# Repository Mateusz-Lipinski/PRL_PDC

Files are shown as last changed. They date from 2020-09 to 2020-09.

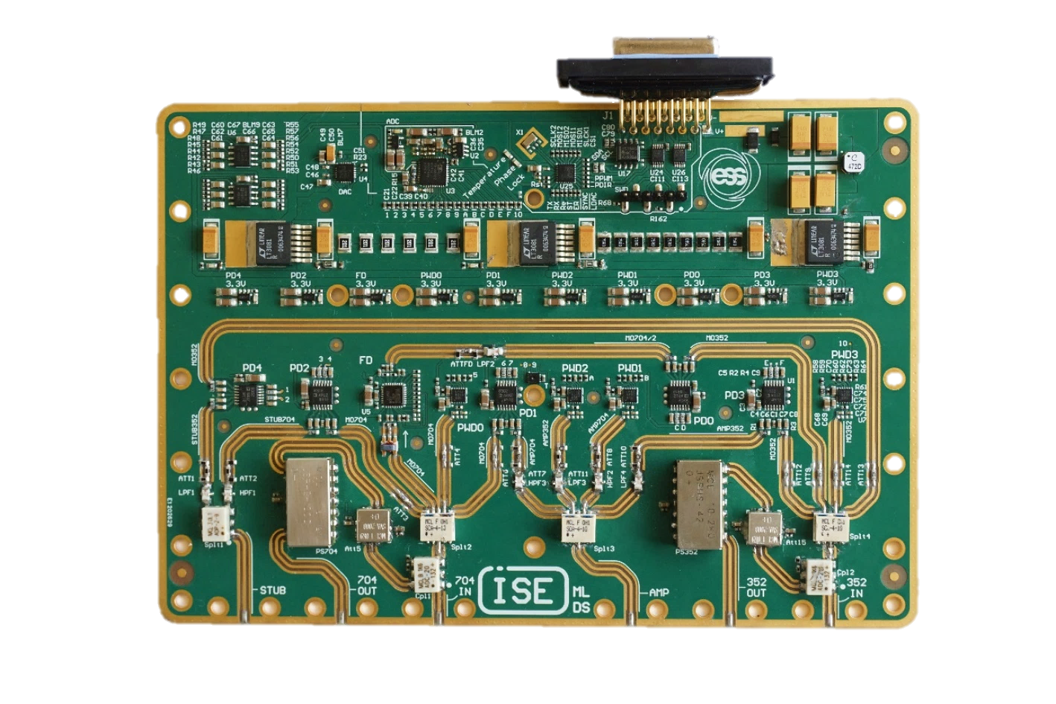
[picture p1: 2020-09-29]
płytka.png

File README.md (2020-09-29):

# PRL_PDC

Działanie układu aktywnej kompensacji dryftów opisałem w swojej pracy magisterskiej. Na płytce dodane są jeszcze regulowane tłumiki przed przesuwnikami fazy, do stabiizacji mocy.

Przesuwniki fazy i tłumiki są sterowane ze wzmacniaczy sumujących 2 sygnały z DAC z różnymi wzmocnieniami, co pozwala na sterowanie zgrubne i precyzyjne, w zakresie 0 - 12V. Wzmacniacze zostały wymienione na wszystkich płytkach i w projekcie, bo poprzednie wymagały symetrycznego zasilania. Innych błędów w projekcie nie znalazłem.
Z tego co wiem to rozwiązanie działa całkiem dobrze. Jak to działa można zobaczyć w symulacji w ./symulations.

Przestrajanie w tak szerokim zakresie jest potrzebne, żeby ustawić punkt stabilizacji w odpowiednim miejscu na charakterystyce detektorów (chyba najlepiej w połowieu)
Wskazania detektorów PD1 i PD2, oraz PD3 i PD4 są ze sobą powiązane, więc napisałem algorytm który przeszukuje charakterystykę i minimalizuje błąd średniokwadratowy, tak żeby oba detektory pracowały jak najbliżej środka charakterystyki. Działa to chyba w miarę ok, ale zdażyło się raz czy dwa że ustawił się taki punkt pracy że sterowanie się nasyciło - zależy od rzeczy podłączonych do układu.

Zauważyłem problem, polegający na tym, że przy przestrajaniu przesuwnika od jednego kanału (na jednej częstotliwości), zmieniaja się również wskazania detektorów na drugiej częstotliwości. Problem występował w prototypie, ale zwarcie wejść sterujących przesuwnikow (mają po 2 wejścia BIAS) wydawało się rozwiązać problem (nie wiem z czego to wynika, tymbardziej że piny wydają się byc zwarte w środku scalaka.
Ja podejrzewam że filtry są za słabe i detektory zbierają też drugą częstotliwość, co wpływa na pomiar fazy. Żeby to potwierdzić trzeba by niestety ciąć ścieżki i dołożyć dodatkowe filtry przed detektorami fazy. Można było zrobić miejsce na to na etapie projektu, ale z jakiegoś powodu podjęliśmy decyzję żeby tego nie robić.
(Minimializacja strat?)

W związku z powyższym, pętle stabilizacji fazy włączane pojedynczo wydają się działać, ale razem - zakłócają się nawzajem. W prototypie powodowało to że dryf fazy nie był kompensowany i wręcz ulegał wzmocnieniu.

Gdy próbowałem uruchomić stabilzację mocy, również występował problem zakłócania się pętli. Zmiana tłumienia powoduje zmianę fazy, a fazy zmianę tłumienia. Przez to obie pętle wariowały. W tym wypadku to jest raczej kwestia nastaw PID.

Stabilizacja temperatury działa, ale nie bardzo daje się schłodzić ten układ, nawet z radiatorem. Stabilizowałem na 35\*C - to trochę dużo. Nie wiem jakie warunki będą w docelowym racku. Precyzja stabilizacji jest bardzo dobra moim zdaniem.

Przy odkręcaniu kabli urywają się złącza SMA - lutowanie chyba pomaga.

Mikrokontroler programuje się przez wewnętrzne złącza SWD za pomocą ST-Link, albo przez uart ze złącza USB na frontpanelu.

Do działania programowania przez uart, wymagane jest założenie zaślepki z kondensatorem i rezystorem na złącze SWD na płytce.
Zaślepkę wymyśliłem niedawno, bo pierwszy raz mam doczynienia z tym bootloaderem. Ale działa. Schemat jest w plikach projektowych obok złącza SWD (RF.schdoc).
Bootloader uart jest aktywny jeśli NAJPIERW podłączymy zasilony kabel USB, a dopiero potem włączymy zasilanie systemu. Więcej na ten temat w readme repozytorim z kodem.

Ze strony mikrokontrolera jest zaprogramowane:
DAC (Wartości ustawiane przez makro),
ADC (Wartości odczytywane ~ co sekundę na przerwaniach) ,
Stablizacja temperatury,
Przeliczanie odczytów z ADC na wartości fizyczne,
Komunikacja po uart (proste komendy),
Optymalizacja punktu pracy detekrorów opisana wyżej (ta funkcja trwa kilka sekund).

Nie są zaprogramowane:
Komunkacja z modułem ethernet przez i2c
Stabiliaja mocy

Dodatkowo nie działa kwarc zegarkowy (pewnie kwestia dobrania kondensatorków), ale nie jest w zasadzie potrzebny, dodałem go w razie czego jakby była potrzebna jakaś lepsza referencja czasu.

Więcej w readme w repozytorum PRL_PDC_Source

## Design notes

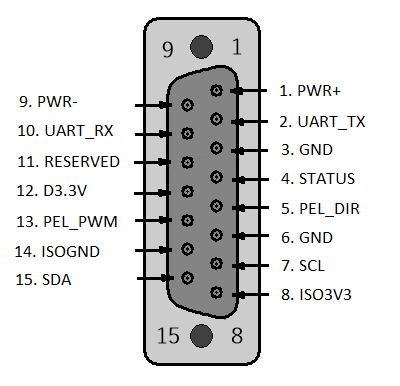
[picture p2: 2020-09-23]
AD19/Projects/Phase Drift Compensation/DB15 PINOUT.png

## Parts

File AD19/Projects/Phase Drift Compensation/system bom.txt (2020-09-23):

RF PSU:		+15V: 	https://www.tme.eu/pl/details/lrs-35-15/zasilacze-do-wbudowania/mean-well/
Pelt+fans PSU:	+12V: 	https://www.tme.eu/pl/details/rs-35-12/zasilacze-do-wbudowania/mean-well/
12V->3.3V DCDC: 	
fans: 		+12V:	https://www.tme.eu/pl/details/mec0251v2-a99/wentylatory-dc-12v/sunon/mec0251v2-000u-a99/
Peltier driver: +12V:  
Peltier:	+12V:	
xtpico:		+3.3V:

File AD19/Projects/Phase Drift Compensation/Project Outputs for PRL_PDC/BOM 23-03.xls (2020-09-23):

Designator | Quantity | Comment | Case | Supplier 1 | Supplier Part Number 1 | Manufacturer | Manufacturer Part Number 1 | Value | Voltage Rating | Dielectric | Tolerance | Description | HelpURL
U7_PWD0, U7_PWD1, U7_PWD2, U7_PWD3 | 4 | LTC5582 | 10-DFN | Digi-Key | LTC5582IDD#PBF-ND | Linear Technology/Analog Devices | LTC5582IDD#PBF |  |  |  |  | 40MHz to 10GHz RMS Power Detector with 57dB Dynamic Range | https://www.analog.com/media/en/technical-documentation/data-sheets/LTC5582.pdf
U17 | 1 | ISO1540DR | 8-SOIC | Digi-Key | 296-34871-1-ND | Texas Instruments | ISO1540DR |  |  |  |  | 12 Weeks Detailed Description I²C Digital Isolator 2500Vrms 2 Channel 1Mbps 25kV/µs CMTI 8-SOIC (0.154", 3.90mm Width) | http://www.ti.com/lit/ds/symlink/iso1540.pdf
BLM1_PD0, BLM1_PD1, BLM1_PD2, BLM1_PD3, BLM1_PD4 | 5 | 1 kOhms @ 100MHz | 402 | Digi-Key | 490-16511-1-ND | Murata Electronics | BLM15AG102SZ1D |  |  |  |  | 1 kOhms @ 100MHz 1 Signal Line Ferrite Bead 0402 (1005 Metric) 300mA 650mOhm | https://www.murata.com/en-us/products/productdata/8796748677150/QNFA9118.pdf
U20, U21, U23 | 3 | ADJ | 7-DDPAK | Digi-Key | LT3081ER#PBF-ND | Linear Technology/Analog Devices | LT3081ER#PBF |  |  |  |  | 1.5A Single Resistor Rugged Linear Regulator with Monitors | analog.com/media/en/technical-documentation/data-sheets/3081fc.pdf
U5 | 1 | AD9515 | LFCSP32 | Digi-Key | AD9515BCPZ-REEL7CT-ND | Analog Devices Inc. | AD9515BCPZ-REEL7 |  |  |  |  | 1.6 GHz Clock Distribution IC, Dividers, Delay Adjust, Two Outputs | https://www.analog.com/media/en/technical-documentation/data-sheets/AD9515.pdf
T1 | 1 | MABAES0061 | MABAES0061 | Digi-Key | 1465-1318-1-ND | M/A-Com Technology Solutions | MABAES0061 |  |  |  |  | 1:4 E-Series, RF Flux Coupled Transformer 2 - 800 MHz | https://cdn.macom.com/datasheets/MABAES0061.pdf
BLM2, BLM3, BLM4, BLM7, BLM8, BLM9_OffsetAmp352, BLM9_OffsetAmp704, BLM10_PWD0, BLM10_PWD1, BLM10_PWD2, BLM10_PWD3, BLM11, BLM12, BLM13, BLM14, BLM15, BLM16 | 17 | 120 Ohms @ 100MHz | 402 | Digi-Key | 490-16510-1-ND | Murata Electronics | BLM15AX121SZ1D |  |  |  |  | 120 Ohms @ 100MHz 1 Power, Signal Line Ferrite Bead 0402 (1005 Metric) 700mA 130mOhm | https://www.murata.com/en-us/products/productdata/8796748677150/QNFA9118.pdf
J1 | 1 | D-Sub |  | Digi-Key | AE10105-ND | Assmann WSW Components | A-DF 15 AA-WP |  |  |  |  | 15 Position D-Sub Plug, Female Pins Connector | http://www.assmann-wsw.com/fileadmin/datasheets/ASS_3251_CO.pdf
C91, C92, C93, C94 | 4 | 150µF | 2917 | Digi-Key | 399-4794-1-ND | KEMET | T491X157K020AT | 150µF | 20V |  | ±10% | 150µF Molded Tantalum Capacitors 20V 2917 | https://content.kemet.com/datasheets/KEM_T2005_T491.pdf
U18_A3.3V_ADC, U18_A3.3V_FD, U18_A3.3V_PD1, U18_A3.3V_PD2, U18_A3.3V_PD3, U18_A3.3V_PD4, U18_A3.3V_PhD1, U18_A3.3V_PhD2, U18_A3.3V_PhD3, U18_A3.3V_PhD4, U18_A3.3V_PhD5 | 11 | 3.3V | TSOT-23-5 | Digi-Key | ADP7118AUJZ-3.3-R7CT-ND | ANALOG DEVICES | ADP7118AUJZ-3.3-R7 | 3.3V |  |  |  | 20 V, 200 mA, Low Noise, CMOS LDO Linear Regulator | https://www.analog.com/media/en/technical-documentation/data-sheets/adp7118.pdf
D2 | 1 | 17.8V | DO-219AB | Digi-Key | SMF16A-E3-08GICT-ND | Vishay Semiconductor Diodes Division | SMF16A-E3-08 |  |  |  |  | 26V Clamp 7.7A Ipp Tvs Diode Surface Mount SMF | http://www.vishay.com/docs/85881/smf5v0atosmf58a.pdf
X1 | 1 | 32.768KHz | 2-SMD | Digi-Key | 535-11937-1-ND | Abracon LLC | ABS07-120-32.768KHZ-T | 32.768KHz |  |  |  | 32.768kHz ±20ppm Crystal 6pF 55 kOhms 2-SMD, No Lead | https://abracon.com/Resonators/ABS07-120-32.768kHz-T.pdf
U24, U26 | 2 | A-ESD | 10-MSOP | Digi-Key | CM1213-08MROSCT-ND | ON Semiconductor | CM1213-08MR |  |  |  |  | 8-Channel Low Capacitance ESD Protection Array | https://www.onsemi.com/pub/Collateral/CM1213-D.PDF
C50 | 1 | 10uF | 1206 | Digi-Key | 399-8269-1-ND | KEMET | T491A106K016AT | 10uF | 16V |  |  | CAP TANT 10UF 10% 16V 1206
C87, C90, C95, C98, C103, C106 | 6 | 10uF | 2312 | Digi-Key | 399-3734-1-ND | KEMET | T491C106K025AT | 10uF | 25V |  |  | CAP TANT 10UF 10% 25V 2312 | https://content.kemet.com/datasheets/KEM_T2005_T491.pdf
D1 | 1 | PMEG6030EVPX | SOD128 | Digi-Key | 1727-1349-1-ND | Nexperia USA Inc. | PMEG6030EVPX |  |  |  |  | Diode Schottky 60V 3A Surface Mount SOD-128/CFP5 | https://assets.nexperia.com/documents/data-sheet/PMEG6030EVP.pdf
U12 | 1 | SHT31-ARP | 8-DFN | Digi-Key | 1649-1012-1-ND | Sensirion AG | SHT31-ARP-B |  |  |  |  | Humidity and Temperature Sensor IC | https://media.digikey.com/pdf/Data%20Sheets/Sensirion%20PDFs/HT_DS_SHT3x_ARP_V3.pdf
U25 | 1 | STM32G071GBU6 | 28-UFQFPN | Digi-Key | 497-18343-ND | STMicroelectronics (https://www.digikey.com/en/supplier-centers/s/stmicroelectronics) | STM32G071GBU6 |  |  |  |  | IC MCU 32BIT 128KB FLASH 28QFPN | https://media.digikey.com/pdf/Data%20Sheets/ST%20Microelectronics%20PDFS/STM32G071_Rev1_DS.pdf
U4 | 1 | AD5676R | 20-WFQFN Exposed Pad, CSP | Digi-Key | AD5676RACPZ-REEL7CT-ND | Analog Devices Inc. | AD5676RACPZ-REEL7 |  |  |  |  | Octal, 16-Bit nanoDAC+ with 2 ppm/°C Reference, SPI Interface | https://www.analog.com/media/en/technical-documentation/data-sheets/ad5672r_5676r.pdf
J2 | 1 | GOLDPIN_1X6 |  | Digi-Key | 1849-1036-ND | METZ CONNECT USA Inc. | PM20206VBNN |  |  |  |  |  | https://www.metz-connect.com/us/system/files/productfiles/Data_sheet_PM202XXVBNN.PDF
U2 | 1 | MAX6071 | SOT23-6 | Farnel | 3257466 | MAXIM INTEGRATED PRODUCTS | MAX6071AAUT18+T |  |  |  |  | Low-Noise, High-Precision Series 1.8V Voltage Reference | https://datasheets.maximintegrated.com/en/ds/MAX6070-MAX6071.pdf
U1_PD0, U1_PD1, U1_PD2, U1_PD3, U1_PD4 | 5 | AD8302 | TSSOP14 | Farnell | 1498702 | ANALOG DEVICES | AD8302ARUZ |  |  |  |  | RF/IF Gain and Phase Detector • LF–2.7 GHz | https://www.analog.com/media/en/technical-documentation/data-sheets/ad8302.pdf
L1 | 1 | 4.7uH | LPD5030 | Farnell | 2434738 | COILCRAFT | LPD5030-472MRB | 4.7uH |  |  |  | Shielded Coupled Inductor | http://www.farnell.com/datasheets/1862246.pdf
U6_OffsetAmp352, U6_OffsetAmp704 | 2 | AD8676 | SOIC8 | Farnell | AD8676ARZ | ANALOG DEVICES | AD8676ARZ |  |  |  |  | Ultra Precision, 36 V, 2.8 nV/√Hz Dual RRO Op Amp | https://www.analog.com/media/en/technical-documentation/data-sheets/AD8676.pdf
C71_PWD0, C71_PWD1, C71_PWD2, C71_PWD3, C73_PWD0, C73_PWD1, C73_PWD2, C73_PWD3, C74_PWD0, C74_PWD1, C74_PWD2, C74_PWD3 | 12 | 1n | 402 |  |  |  |  | 1n | 16V | X7R/C0G | ±20% | Capacitor 0402
C1_PD0, C1_PD1, C1_PD2, C1_PD3, C1_PD4, C54, C55, C56, C58, C59, C77, C83, C118, C119, C120, C121, C122, C123, C124, C125 | 20 | 100n | 402 |  |  |  |  | 100n | 16V | X7R/C0G | ±20% | Capacitor 0402
C66_OffsetAmp352, C66_OffsetAmp704, C108, C112 | 4 | 100nF | 402 |  |  |  |  | 100nF | 16V | X7R/C0G | ±20% | Capacitor 0402
C14, C15, C20, C23, C24, C25, C26, C27, C28, C29, C30, C31, C32, C33, C34, C37 | 16 | 470n | 402 |  |  |  |  | 470n | 16V | X7R/C0G | ±20% | Capacitor 0402
C111, C113 | 2 | 470nF | 402 |  |  |  |  | 470nF | 16V | X7R/C0G | ±20% | Capacitor 0402
R22, R30, R31, R32, R33, R34, R35, R37, R38, R43_OffsetAmp352, R43_OffsetAmp704, R51_OffsetAmp352, R51_OffsetAmp704, R59_PWD0, R59_PWD1, R59_PWD2, R59_PWD3, R60_PWD0, R60_PWD1, R60_PWD2, R60_PWD3, R62_PWD0, R62_PWD1, R62_PWD2, R62_PWD3, R153 | 26 | 0r | 402 |  |  |  |  | 0r |  |  | ±1% | Resistor 0402
R63_PWD0, R63_PWD1, R63_PWD2, R63_PWD3, R97, R99 | 6 | 1k | 402 |  |  |  |  | 1k |  |  | ±1% | Resistor 0402
R64_PWD0, R64_PWD1, R64_PWD2, R64_PWD3, R68, R70_A3.3V_ADC, R70_A3.3V_FD, R70_A3.3V_PD1, R70_A3.3V_PD2, R70_A3.3V_PD3, R70_A3.3V_PD4, R70_A3.3V_PhD1, R70_A3.3V_PhD2, R70_A3.3V_PhD3, R70_A3.3V_PhD4, R70_A3.3V_PhD5, R71, R76, R104 | 19 | 2k | 402 |  |  |  |  | 2k |  |  | ±1% | Resistor 0402
R44_OffsetAmp352, R44_OffsetAmp704, R48_OffsetAmp352, R48_OffsetAmp704, R52_OffsetAmp352, R52_OffsetAmp704, R56_OffsetAmp352, R56_OffsetAmp704 | 8 | 2.4k | 402 |  |  |  |  | 2.4k |  |  | ±1% | Resistor 0402
R24, R27 | 2 | 4.12k | 402 |  |  |  |  | 4.12k |  |  | ±1% | Resistor 0402
R45_OffsetAmp352, R45_OffsetAmp704, R47_OffsetAmp352, R47_OffsetAmp704, R54_OffsetAmp352, R54_OffsetAmp704, R55_OffsetAmp352, R55_OffsetAmp704 | 8 | 9.1k | 402 |  |  |  |  | 9.1k |  |  | ±1% | Resistor 0402
R23, R46_OffsetAmp352, R46_OffsetAmp704, R49_OffsetAmp352, R49_OffsetAmp704, R53_OffsetAmp352, R53_OffsetAmp704, R57_OffsetAmp352, R57_OffsetAmp704, R93 | 10 | 10k | 402 |  |  |  |  | 10k |  |  | ±1% | Resistor 0402
R5, R6, R7, R8, R9, R10, R11, R12, R13, R14, R16, R17, R18, R19, R20, R21 | 16 | 33k | 402 |  |  |  |  | 33k |  |  | ±1% | Resistor 0402
R156 | 1 | 49.9r | 402 |  |  |  |  | 49.9r |  |  | ±1% | Resistor 0402
R83, R84, R85, R86, R87, R88, R89, R90, R91, R92, R94, R95, R96, R98, R100, R101, R102, R103, R105, R106, R107 | 21 | 50r | 402 |  |  |  |  | 50r |  |  | ±1% | Resistor 0402
R61_PWD0, R61_PWD1, R61_PWD2, R61_PWD3 | 4 | 68r | 402 |  |  |  |  | 68r |  |  | ±1% | Resistor 0402
R162 | 1 | 100k | 402 |  |  |  |  | 100k |  |  | ±1% | Resistor 0402
R65, R69, R154, R155, R26, R40 | 6 | 100r | 402 |  |  |  |  | 100r |  |  | ±1% | Resistor 0402
R25, R36 | 2 | 200r | 402 |  |  |  |  | 200r |  |  | ±1% | Resistor 0402
C69_PWD0, C69_PWD1, C69_PWD2, C69_PWD3 | 4 | 1n | 603 |  |  |  |  | 1n | 16V | X7R/C0G | ±20% | Capacitor 0603
C4_PD0, C4_PD1, C4_PD2, C4_PD3, C4_PD4, C5_PD0, C5_PD1, C5_PD2, C5_PD3, C5_PD4, C6_PD0, C6_PD1, C6_PD2, C6_PD3, C6_PD4, C7_PD0, C7_PD1, C7_PD2, C7_PD3, C7_PD4, C8_PD0, C8_PD1, C8_PD2, C8_PD3, C8_PD4, C9_PD0, C9_PD1, C9_PD2, C9_PD3, C9_PD4 | 30 | 1nF | 603 |  |  |  |  | 1nF | 16V | X7R/C0G | ±20% | Capacitor 0603
C2_PD0, C2_PD1, C2_PD2, C2_PD3, C2_PD4, C53 | 6 | 1uF | 603 |  |  |  |  | 1uF | 16V | X7R/C0G | ±20% | Capacitor 0603
C70_PWD0, C70_PWD1, C70_PWD2, C70_PWD3 | 4 | 100n | 603 |  |  |  |  | 100n | 16V | X7R/C0G | ±20% | Capacitor 0603
C76, C78, C114, C115, C116, C117 | 6 | 100nF | 603 |  |  |  |  | 100nF | 16V | X7R/C0G | ±20% | Capacitor 0603
R2_PD0, R2_PD1, R2_PD2, R2_PD3, R2_PD4, R4_PD0, R4_PD1, R4_PD2, R4_PD3, R4_PD4, R121, R124, R127, R136, R139, R145, R151 | 17 | 0r | 603 |  |  |  |  | 0r |  |  | ±1% | Resistor 0603
R66, R67, R108, R109 | 4 | 1.5k | 603 |  |  |  |  | 1.5k |  |  | ±1% | Resistor 0603
R58_PWD0, R58_PWD1, R58_PWD2, R58_PWD3 | 4 | 1.5r | 603 |  |  |  |  | 1.5r |  |  | ±1% | Resistor 0603
R15 | 1 | 10k | 603 |  |  |  |  | 10k |  |  | ±1% | Resistor 0603
R133, R148 | 2 | 44.2r | 603 |  |  |  |  | 44.2r |  |  | ±1% | Resistor 0603
R1_PD0, R1_PD1, R1_PD2, R1_PD3, R1_PD4, R3_PD0, R3_PD1, R3_PD2, R3_PD3, R3_PD4 | 10 | 52.3r | 603 |  |  |  |  | 52.3r |  |  | ±1% | Resistor 0603
R114, R116 | 2 | 53.6r | 603 |  |  |  |  | 53.6r |  |  | ±1% | Resistor 0603
R111, R113, R117, R119 | 4 | 54.9r | 603 |  |  |  |  | 54.9r |  |  | ±1% | Resistor 0603
R130 | 1 | 56.2r | 603 |  |  |  |  | 56.2r |  |  | ±1% | Resistor 0603
R142 | 1 | 63.4r | 603 |  |  |  |  | 63.4r |  |  | ±1% | Resistor 0603
R141, R143 | 2 | 105r | 603 |  |  |  |  | 105r |  |  | ±1% | Resistor 0603
R129, R131 | 2 | 107r | 603 |  |  |  |  | 107r |  |  | ±1% | Resistor 0603
R132, R134, R147, R149 | 4 | 130r | 603 |  |  |  |  | 130r |  |  | ±1% | Resistor 0603
R112 | 1 | 442r | 603 |  |  |  |  | 442r |  |  | ±1% | Resistor 0603
R118 | 1 | 562r | 603 |  |  |  |  | 562r |  |  | ±1% | Resistor 0603
R115 | 1 | 590r | 603 |  |  |  |  | 590r |  |  | ±1% | Resistor 0603
LED1_A3.3V_ADC, LED1_A3.3V_FD, LED1_A3.3V_PD1, LED1_A3.3V_PD2, LED1_A3.3V_PD3, LED1_A3.3V_PD4, LED1_A3.3V_PhD1, LED1_A3.3V_PhD2, LED1_A3.3V_PhD3, LED1_A3.3V_PhD4, LED1_A3.3V_PhD5, LED2, LED3, LED4, LED5 | 15 | Red | 603 |  |  |  |  |  |  |  |  | Led 0603 red
C12, C18, C21, C35, C39, C44, C47, C49, C67_OffsetAmp352, C67_OffsetAmp704, C68_PWD0, C68_PWD1, C68_PWD2, C68_PWD3, C107 | 15 | 1uF | 805 |  |  |  |  | 1uF | 16V | X7R/C0G | ±20% | Capacitor 0805
C60_OffsetAmp352, C60_OffsetAmp704, C61_OffsetAmp352, C61_OffsetAmp704, C62_OffsetAmp352, C62_OffsetAmp704, C63_OffsetAmp352, C63_OffsetAmp704, C64_OffsetAmp352, C64_OffsetAmp704, C65_OffsetAmp352, C65_OffsetAmp704 | 12 | 2.2uF | 805 |  |  |  |  | 2.2uF | 16V | X7R/C0G | ±20% | Capacitor 0805
R77 | 1 | 66.5k | 805 |  |  |  |  | 66.5k |  |  | ±1% | Resistor 0805
R161 | 1 | 100k | 805 |  |  |  |  | 100k |  |  | ±1% | Resistor 0805
R160 | 1 | 240k | 805 |  |  |  |  | 240k |  |  | ±1% | Resistor 0805
C3_PD0, C3_PD1, C3_PD2, C3_PD3, C3_PD4, C13, C19, C52, C81_A3.3V_ADC, C81_A3.3V_FD, C81_A3.3V_PD1, C81_A3.3V_PD2, C81_A3.3V_PD3, C81_A3.3V_PD4, C81_A3.3V_PhD1, C81_A3.3V_PhD2, C81_A3.3V_PhD3, C81_A3.3V_PhD4, C81_A3.3V_PhD5, C82_A3.3V_ADC, C82_A3.3V_FD, C82_A3.3V_PD1, C82_A3.3V_PD2, C82_A3.3V_PD3, C82_A3.3V_PD4, C82_A3.3V_PhD1, C82_A3.3V_PhD2, C82_A3.3V_PhD3, C82_A3.3V_PhD4, C82_A3.3V_PhD5 | 30 | 10uF | 1206 |  |  |  |  | 10uF | 16V | X7R/C0G | ±20% | Capacitor 1206
R78, R79, R80, R81, R82, R157, R158, R159, R163 | 9 | 75r | 1210 |  |  |  |  | 75r |  |  | ±1% | Resistor 1210
R28, R29, R72, R73, R74, R75 | 6 | 200r | 1210 |  |  |  |  | 200r |  |  | ±1% | Resistor 1210
To be shipped with (no assembly): | 1 per PCB | D SUB CONNECTOR |  | Digi-Key | 609-1425-ND | Amphenol ICC (FCI) | 86303638BLF |  |  |  |  | 15 Position Hinged Backshell Connector Black 180° Unshielded | http://www.amphenol-icc.com/media/wysiwyg/files/drawing/10061215.pdf
EXCLUDED FROM BOM:
SMA1, SMA2, SMA3, SMA4, SMA5, SMA6 | 1 |  |  | Farnell | 2253765 | MULTICOMP PRO | MC000242 |  |  |  |  | SMA Bulkhead Jack Front Mount | http://www.farnell.com/datasheets/1686097.pdf
U3 | 1 | AD7173-8 | LFCSP40 | Farnell | 2377349 | ANALOG DEVICES | AD7173-8BCPZ |  |  |  |  | Highly Integrated 24 Bit Sigma-Delta ADC 8-/16-Channel Low Power 31.25 kSPS | https://www.analog.com/media/en/technical-documentation/data-sheets/AD7173-8.pdf
Cpl1, Cpl2 | 2 | ADC-20-132+ | CD542 | Mini-Circuits | ADC-20-132+ |  |  |  |  |  |  | 20 dB SMT Directional Coupler, 100 - 1300 MHz, 50Ω | https://www.minicircuits.com/pdfs/ADC-20-132+.pdf
HPF1, HPF2, HPF3 | 3 | HFCN-650 | FV1206 | Mini-Circuits | HFCN-650 |  |  |  |  |  |  | Ceramic High Pass Filter • 50Ω • 710 to 2490 MHz | https://www.minicircuits.com/pdfs/HFCN-650.pdf
LPF1, LPF2, LPF3, LPF4 | 4 | LFCN-400 | FV1206 | Mini-Circuits | LFCN-400 |  |  |  |  |  |  | Ceramic Low Pass Filter • 50Ω • DC to 400 MHz | https://ww2.minicircuits.com/pdfs/LFCN-400.pdf
PS352 | 1 | JSPHS-42+ | BK276 | Mini-Circuits | JSPHS-42+ |  |  |  |  |  |  | Narrow Band Phase Shifter • 50 Ohm • 180 deg Voltage Variable • 300 MHz to 400 MHz | https://ww2.minicircuits.com/pdfs/JSPHS-42+.pdf
PS704 | 1 | JSPHS-1000+ | BK276 | Mini-Circuits | JSPHS-1000+ |  |  |  |  |  |  | Narrow Band Phase Shifter • 50 Ohm • 180 deg Voltage Variable • 700 MHz to 1000 MHz | https://ww2.minicircuits.com/pdfs/JSPHS-1000+.pdf
Splt1 | 1 | ADP-2-9+ | CD636 | Mini-Circuits | ADP-2-9+ |  |  |  |  |  |  | Power Splitter/Combiner • 2 Way-0° • 50Ω • 200 to 900 MHz | https://ww2.minicircuits.com/pdfs/ADP-2-9+.pdf
Splt2, Splt3, Splt4 | 3 | SCA-4-10+ | DZ943 | Mini-Circuits | SCA-4-10+ |  |  |  |  |  |  | Power Splitter/Combiner • 4 Way • 50Ω • 5 to 1000 MHz | https://www.minicircuits.com/pdfs/SCA-4-10+.pdf
Att5, Att15 | 2 | SVA-2000+ | FZ990 | Mini-Circuits | SVA-2000+ |  |  |  |  |  |  | Voltage Variable Attenuator 50Ω 50 to 2000 MHz | https://www.minicircuits.com/pdfs/SVA-2000+.pdf
